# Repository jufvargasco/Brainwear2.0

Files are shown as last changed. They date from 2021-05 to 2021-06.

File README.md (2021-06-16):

# Brainwear board

The Brainwear board is an open-source EEG sensing driver module is designed with the state-of-the-art analog front-end that is pin-compatible with the popular Feather ecosystem in the wearable and DIY community.

## Hardware description

The Brainwear board was made using the Texas Instruments Analog Front-End ADS1299. This SOC incorporates low-power technology and integrates instrumentation amplifiers, operational amplifiers, and analog to digital converters into a single IC. Hence, it is ideal for biopotential measurements such as EEG, ECG, and EOG as it provides eight different channels with a 24-bit resolution and a sampling rate of 250 Hz. Additionally, it includes attractive characteristics such as test signals for impedance measurement and SPI compatible interface.

The Brainwear board is a mixed-signal system that combines both analog and digital components. Since both components are present in a single circuit, the analog circuit is susceptible to crosstalk noise generated by the digital circuit via stray capacitances. As a result, the small EEG signals acquired by the AFE can easily be distorted and provide erroneous measurements. The crosstalk noise was avoided by using a fully isolated circuit design technique. That is, separated ground planes for digital and analog signals and isolated analog and digital interfaces at each side of the board. Moreover, we used Low-Dropout linear regulators (MCP1754T-3302, TPS72325, TLV70025) and a voltage inverter (TCM828) to provide the analog bipolar supply of +- 2.5V and the digital supply of + 3.3V. The control signals of these devices were also isolated from the ground planes to avoid the switching noise generated by the voltage inverter.  

The feather board powers the Brainwear board. Then, a voltage detection IC (BD5330G) is used to disconnect the circuit once the supply voltage is lower than 3V to protect the battery. The ADS1299 is connected in a referential montage. Thus, eight different channels can be measured in reference to the input SRB1. The AFE also offers the possibility of measuring the bias in the signals using the Bias input included in the PCB. Electrostatic discharge chips were included to protect the channels of the board as well as the main analog and digital signals in the circuit.
Additionally, an LED (GPIO4) was added to provide an easy way to test the SPI communication between the main board and the Brainwear module. Hardware filters were included following the references provided by Texas Instruments and OpenBCI. Finally, an SD module was integrated into the board in order to record EEG data when required. It is essential to mention that the ADS1299 and the SD card do not share the same SPI bus. Hence, the ADS1299 is connected to the predetermined SPI pins of the feather board, while the SD card requires configuring the board's upper pins to act as an SPI bus.

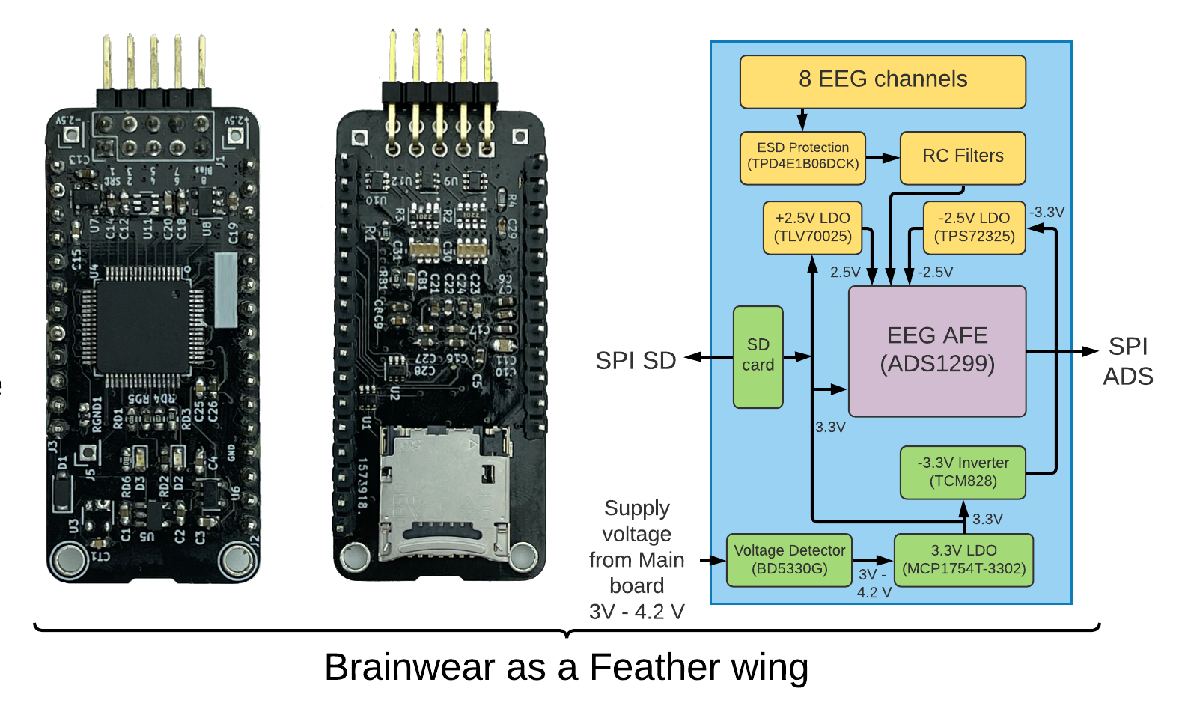
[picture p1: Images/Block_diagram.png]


The KiCAD files with the PCB of the Brainwear board are in the folder Design Files

## Firmware description
The firmware shows an application example in the file Brainwear_test.ino. The program contains two different types of classes: the first one is used for instantiating the Brainwear board while the second allows to add the Mechanomyography sensors whose signals are acquired with the TI-ADS1015. The first class packages all the functionalities available in the Brainwear hardware, i.e. testing signals, register, channel, and sample rate configuration, among others. This code is based on the OpenBCI firmware for the Cyton board. On the other hand, the second class allows to instantiate one board of the ADS1015 according to the required sample rate and gain. It also includes functionalities to send data to the main board according to the type of transmissions.

The system receives commands via the serial port that allow to configure the way the board behaves. A description of the commands is given below. Further information about the commands can be found in the file Brainwear_definitions.h

### Commands
#### Multichar commands
1. Channel settings

This command requires multiple characters to be recognized. It consists of seven different settings group together corresponding to the channel to modify, power-down, gain, type of input, bias generation, connection to SRB2, connection to SRB1, respectively. The code starts with lower x and end with capital X.

Example:
<p align="center">
    x1060001X
</p>

This code sets the channel (1) to power-down on (0), gain of 24 (6), normal input (0), remove bias (0), disconnected of SRB2 (0) and connected to SRB1 (1)

2. Leadoff settings

This command requires multiple characters to be recognized. It consists of 3 different settings group together corresponding to the channel to modify and the activation of the Lead off for the channel P and the channel N of the specified channel, respectively. The code starts with lower z and end with capital Z.

Example:
<p align="center">
    z111Z
</p>

This code sets the Leadoff detection for the channel (1) to (1 / activated) for the P channel and to (1 / activated) for the N channel.

3. Sample rate settings
 
This command requires multiple characters to be recognized. It consists of the character ~ followed by the desired sample rate for the board. The options are shown below.

| Command | Sample Rate |
|---------|-------------|
| 0       | 16 KHz      |
| 1       | 8 KHz       |
| 2       | 4 KHz       |
| 3       | 2 KHz       |
| 4       | 1 KHz       |
| 5       | 500 Hz      |
| 6       | 250 Hz      |

Example:
<p align="center">
    ~6
</p>

This code sets the sample rate of the board to 250 Hz.

#### Single commands

The single commands to manipulate the Brainwear board as described in the following table.

| Command | Description |
|---------|-------------|
| 1       | Deactivate channel 1      |
| 2       | Deactivate channel 2      |
| 3       | Deactivate channel 3      |
| 4       | Deactivate channel 4      |
| 5       | Deactivate channel 5      |
| 6       | Deactivate channel 6      |
| 7       | Deactivate channel 7      |
| 8       | Deactivate channel 8      |
| Q       | Activate channel 1        |
| W       | Activate channel 2        |
| E       | Activate channel 3        |
| R       | Activate channel 4        |
| T       | Activate channel 5        |
| Y       | Activate channel 6        |
| U       | Activate channel 7        |
| I       | Activate channel 8        |
| p       | Connect channels to DC Test signal      | 
| 0       | Connect channels to GND Test signal     | 
| =       | Connect channels to fast 1X Test signal | 
| -       | Connect channels to slow 1X signal      | 
| ]       | Connect channels to fast 2X Test signal | 
| \[      | Connect channels to slow 2X Test signal | 
| n       | Connect channels to normal input        | 
| d       | Set all channels to default settings      |
| D       | Report the default settings        |
| C       | Report number of channels in board      |
| t       | Activate serial stream of data       |
| y       | Deactivate serial stream of data       |
| b       | Start streaming data       |
| s       | Stop streaming data         |
| ?       | Show the register settings of the ADS1299 board       |
| v       | Soft reset of the board        |
| V       | Get firmware version        |
| l       | Turn on LED on the Brainwear board      |
| k       | Turn off LED on the Brainwear board      |
| a       | Activate recording with the SD card      |
| r       | Reset file counter for the SD files      |
| j       | Close SD file      |
| A       | Record 1 minute of activity in the SD      |
| S       | Record 5 minutes of activity in the SD       |
| F       | Record 15 minutes of activity in the SD      |
| G       | Record 30 minutes of activity in the SD         |
| H       | Record 1 hour of activity in the SD        |
| J       | Record 2 hours of activity in the SD        |
| K       | Record 4 hours of activity in the SD         |
| <       | Set transmission to RAW mode (compatible with OpenBCI)        |
| >       | Set transmission to ASCII mode (compatible with Arduino plotter)        |
| M       | Activate multimode (EEG + MMG)       |
| N       | Deactivate multimode  (Only EEG is active)       |

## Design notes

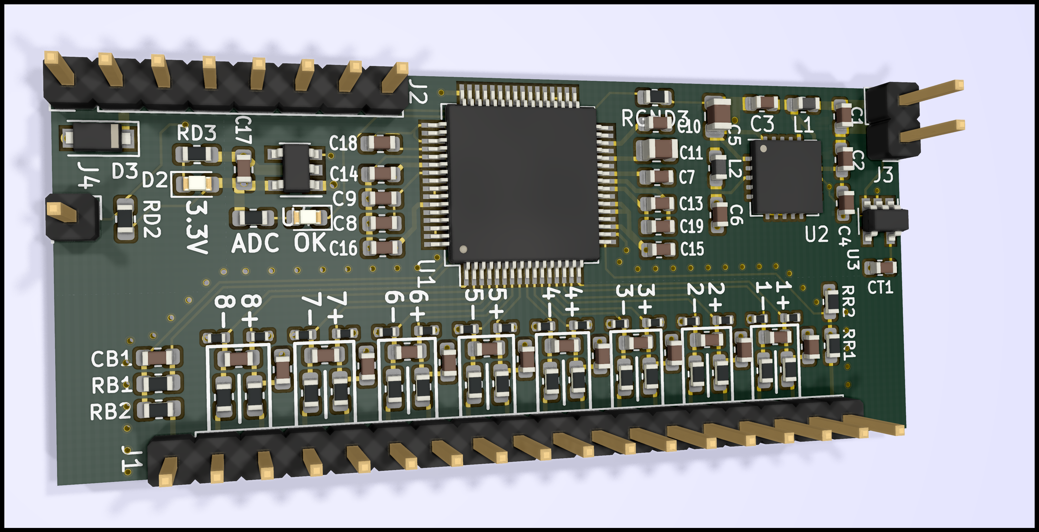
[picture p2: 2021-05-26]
Design files/front ray tracing.png

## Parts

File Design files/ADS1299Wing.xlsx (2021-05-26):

Id | Designator | Package | Quantity | Designation | Voltage | Supplier and ref
1 | -2.5V|+2.5V|J5 | PinHeader_1x01_P2.54mm_Vertical | 3 | Conn_01x01
2 | C1 | C_0603_1608Metric | 1 | 2.2uF | 16
3 | C2|C13|C14|C19|C20 | C_0603_1608Metric | 5 | 2.2uF | 6.3
4 | C10 | C_0805_2012Metric | 1 | 100uF | 6.3
5 | C15 | C_0603_1608Metric | 1 | 0.01uF | 16
6 | C18|C6|C3|C4|C12 | C_0603_1608Metric | 5 | 10uF | 4
7 | C29|CB1|CT1 | C_0603_1608Metric | 3 | 1nF | 16
8 | C31|C30 | CA064C102K5RACTU | 2 | CA064C102K5RACTU
9 | C5|C27|C9|C11|C16|C21|C23|C25 | C_0603_1608Metric | 8 | 1uF | 6.3
10 | C7|C17|C22|C24|C26|C28 | C_0603_1608Metric | 6 | 0.1uF | 16
11 | C8 | C_0603_1608Metric | 1 | 100nF | 16
12 | D1 | D_SOD-123F | 1 | MBR120
13 | D2|D3 | LED_0603_1608Metric | 2 | LED_Small
14 | J1 | PinHeader_2x05_P2.54mm_Vertical | 1 | Conn_02x05_Top_Bottom
15 | J2 | 1X16_ROUND_MIN | 1 | Conn_01x16
16 | J3 | 1X12_ROUND_MIN | 1 | Conn_01x12
17 | R2|R3 | RESCAF80P320X160X60-8N | 2 | CAY16-2201F4LF
18 | R4|R1 | R_0603_1608Metric | 2 | 2.2K
19 | RB1 | R_0603_1608Metric | 1 | 1MOhm
20 | RD1 | R_0603_1608Metric | 1 | 1M
21 | RD2 | R_0603_1608Metric | 1 | 470
22 | RD3|RD4|RD5 | R_0603_1608Metric | 3 | 10K
23 | RD6 | R_0603_1608Metric | 1 | 1k
24 | RGND1 | R_0603_1608Metric | 1 | R_Small
25 | U12|U1|U2|U9|U10|U11 | SOT-363_SC-70-6 | 6 | TPD4E1B06DCK
26 | U3 | SOT-23-5 | 1 | BD5332G
27 | U4 | TQFP-64_10x10mm_P0.5mm | 1 | ADS1299
28 | U5 | SOT95P280X145-5N | 1 | MCP1754T-3302E_OT
29 | U6 | SOT-23-5 | 1 | TCM828
30 | U7 | SOT-23-5 | 1 | TPS72325
31 | U8 | SOT-23-5 | 1 | TLV70025

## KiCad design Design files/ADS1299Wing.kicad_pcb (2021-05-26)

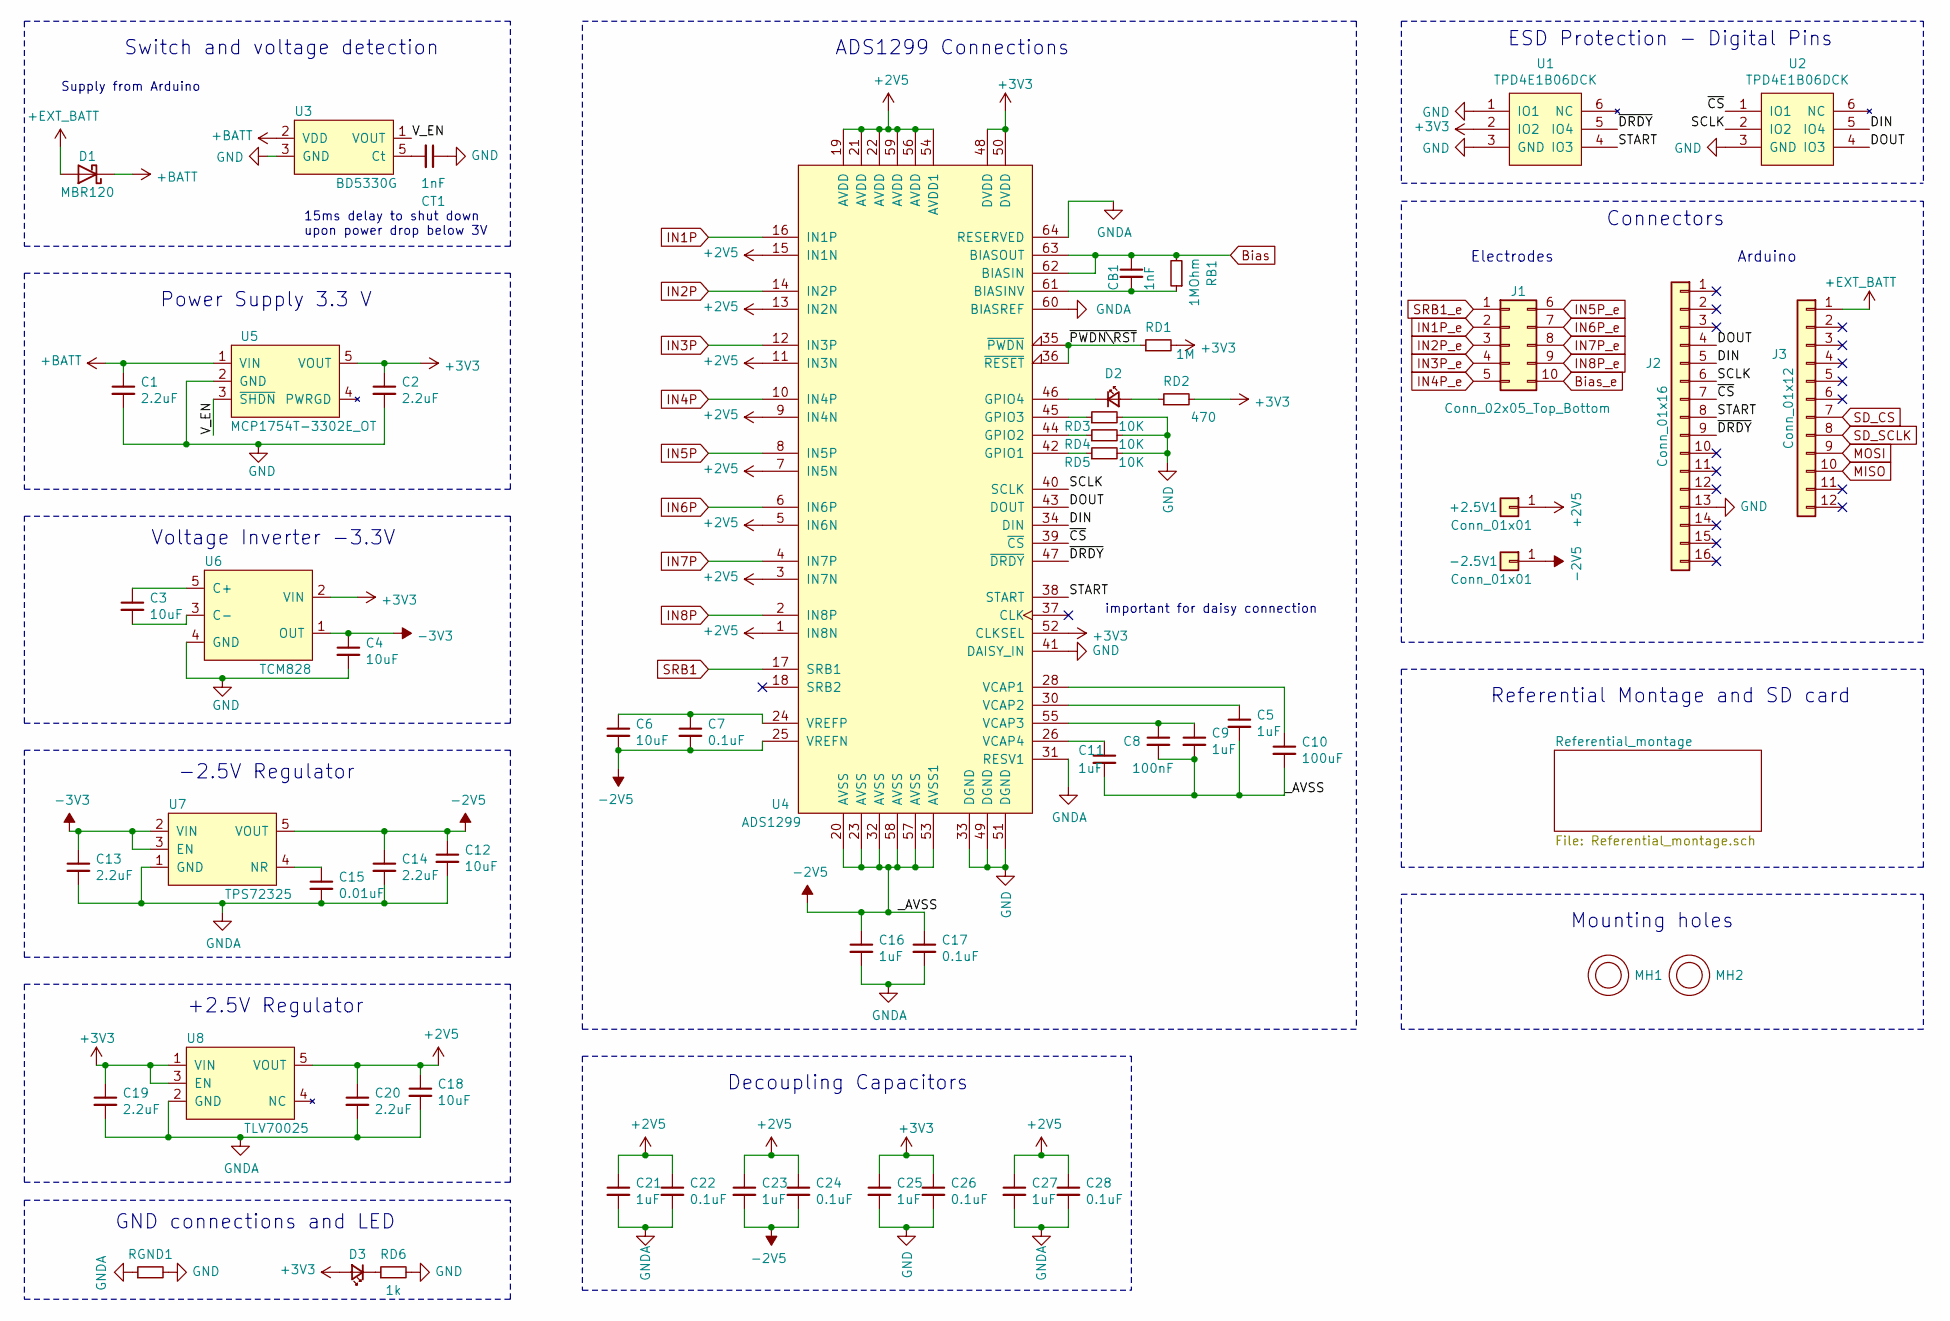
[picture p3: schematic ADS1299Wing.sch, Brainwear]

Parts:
+2.5V1: Conn_01x01; PinHeader_1x01_P2.54mm_Vertical
-2.5V1: Conn_01x01; PinHeader_1x01_P2.54mm_Vertical
C1, C2, C13, C14, C19, C20: 2.2uF; C_0603_1608Metric
C3, C4, C6, C12, C18: 10uF; C_0603_1608Metric
C5, C9, C11, C16, C21, C23, C25, C27: 1uF; C_0603_1608Metric
C7, C17, C22, C24, C26, C28: 0.1uF; C_0603_1608Metric
C8: 100nF; C_0603_1608Metric
C10: 100uF; C_0805_2012Metric
C15: 0.01uF; C_0603_1608Metric
CB1: 1nF; C_0603_1608Metric
CT1: 1nF; C_0603_1608Metric
D1: MBR120; D_SOD-123F
D2, D3: LED_Small; LED_0603_1608Metric
J1: Conn_02x05_Top_Bottom; PinHeader_2x05_P2.54mm_Vertical
J2: Conn_01x16; 1X16_ROUND_MIN
J3: Conn_01x12; 1X12_ROUND_MIN
MH1, MH2: M_HOLE2.5; MH2.5
RB1: 1MOhm; R_0603_1608Metric
RD1: 1M; R_0603_1608Metric
RD2: 470; R_0603_1608Metric
RD3, RD4, RD5: 10K; R_0603_1608Metric
RD6: 1k; R_0603_1608Metric
RGND1: R_Small; R_0603_1608Metric
U1, U2: TPD4E1B06DCK; SOT-363_SC-70-6
U3: BD5330G; SOT-23-5
U4: ADS1299; TQFP-64_10x10mm_P0.5mm
U5: MCP1754T-3302E_OT; SOT95P280X145-5N
U6: TCM828; SOT-23-5
U7: TPS72325; SOT-23-5
U8: TLV70025; SOT-23-5

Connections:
+2V5: +2.5V1.1, C18.1, C20.1, C21.1, C22.1, C23.1, C24.1, C27.1, C28.1, U4.1 (IN8N), U4.3 (IN7N), U4.5 (IN6N), U4.7 (IN5N), U4.9 (IN4N), U4.11 (IN3N), U4.13 (IN2N), U4.15 (IN1N), U4.19 (AVDD), U4.21 (AVDD), U4.22 (AVDD), U4.54 (AVDD1), U4.56 (AVDD), U4.59 (AVDD), U8.5 (VOUT); also elsewhere on the board
+3V3: C2.1, C19.1, C25.1, C26.1, D3.2 (A), RD1.2, RD2.2, U1.2 (IO2), U4.48 (DVDD), U4.50 (DVDD), U4.52 (CLKSEL), U5.5 (VOUT), U6.2 (VIN), U8.1 (VIN), U8.3 (EN); also elsewhere on the board
+BATT: C1.1, D1.1 (K), U3.2 (VDD), U5.1 (VIN)
+EXT_BATT: D1.2 (A), J3.1
-2V5: -2.5V1.1, C5.2, C6.2, C7.2, C8.2, C9.2, C10.2, C11.2, C12.1, C14.1, C16.1, C17.1, C23.2, C24.2, U4.20 (AVSS), U4.23 (AVSS), U4.25 (VREFN), U4.32 (AVSS), U4.53 (AVSS1), U4.57 (AVSS), U4.58 (AVSS), U7.5 (VOUT); also elsewhere on the board
-3V3: C4.1, C13.1, U6.1 (OUT), U7.2 (VIN), U7.3 (EN)
/DIN: J2.5, U2.5 (IO4), U4.34 (DIN)
/DOUT: J2.4, U2.4 (IO3), U4.43 (DOUT)
/SCLK: J2.6, U2.2 (IO2), U4.40 (SCLK)
/START: J2.8, U1.4 (IO3), U4.38 (START)
/V_EN: U3.1 (VOUT), U5.3 (~SHDN)
/~CS: J2.7, U2.1 (IO1), U4.39 (~CS)
/~DRDY: J2.9, U1.5 (IO4), U4.47 (~DRDY)
/~PWDN\RST: RD1.1, U4.35 (~PWDN), U4.36 (~RESET)
Bias: CB1.1, RB1.2, U4.62 (BIASIN), U4.63 (BIASOUT); also elsewhere on the board
Bias_e: J1.10; also elsewhere on the board
GND: C1.2, C2.2, C4.2, C25.2, C26.2, CT1.1, J2.13, RD3.2, RD4.2, RD5.2, RD6.2, RGND1.2, U1.1 (IO1), U1.3 (GND), U2.3 (GND), U3.3 (GND), U4.33 (DGND), U4.41 (DAISY_IN), U4.49 (DGND), U4.51 (DGND), U5.2 (GND), U6.4 (GND); also elsewhere on the board
GNDA: C12.2, C13.2, C14.2, C15.2, C16.2, C17.2, C18.2, C19.2, C20.2, C21.2, C22.2, C27.2, C28.2, RGND1.1, U4.31 (RESV1), U4.60 (BIASREF), U4.64 (RESERVED), U7.1 (GND), U8.2 (GND); also elsewhere on the board
IN1P: U4.16 (IN1P); also elsewhere on the board
IN1P_e: J1.2; also elsewhere on the board
IN2P: U4.14 (IN2P); also elsewhere on the board
IN2P_e: J1.3; also elsewhere on the board
IN3P: U4.12 (IN3P); also elsewhere on the board
IN3P_e: J1.4; also elsewhere on the board
IN4P: U4.10 (IN4P); also elsewhere on the board
IN4P_e: J1.5; also elsewhere on the board
IN5P: U4.8 (IN5P); also elsewhere on the board
IN5P_e: J1.6; also elsewhere on the board
IN6P: U4.6 (IN6P); also elsewhere on the board
IN6P_e: J1.7; also elsewhere on the board
IN7P: U4.4 (IN7P); also elsewhere on the board
IN7P_e: J1.8; also elsewhere on the board
IN8P: U4.2 (IN8P); also elsewhere on the board
IN8P_e: J1.9; also elsewhere on the board
MISO: J3.10; also elsewhere on the board
MOSI: J3.9; also elsewhere on the board
unnamed: C3.1, U6.5 (C+)
unnamed: C3.2, U6.3 (C-)
unnamed: C5.1, U4.30 (VCAP2)
unnamed: C6.1, C7.1, U4.24 (VREFP)
unnamed: C8.1, C9.1, U4.55 (VCAP3)
unnamed: C10.1, U4.28 (VCAP1)
unnamed: C11.1, U4.26 (VCAP4)
unnamed: C15.1, U7.4 (NR)
unnamed: CB1.2, RB1.1, U4.61 (BIASINV)
unnamed: CT1.2, U3.5 (Ct)
unnamed: D2.1 (K), U4.46 (GPIO4)
unnamed: D2.2 (A), RD2.1
unnamed: D3.1 (K), RD6.1
unnamed: RD3.1, U4.45 (GPIO3)
unnamed: RD4.1, U4.44 (GPIO2)
unnamed: RD5.1, U4.42 (GPIO1)
SD_CS: J3.7; also elsewhere on the board
SD_SCLK: J3.8; also elsewhere on the board
SRB1: U4.17 (SRB1); also elsewhere on the board
SRB1_e: J1.1; also elsewhere on the board

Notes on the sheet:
15ms delay to shut down upon power drop below 3V
Power Supply 3.3 V
Switch and voltage detection
Voltage Inverter -3.3V
-2.5V Regulator
+2.5V Regulator
ADS1299 Connections
ESD Protection - Digital Pins
GND connections and LED
Connectors
Electrodes
Arduino
important for daisy connection
Supply from Arduino
Referential Montage and SD card
Decoupling Capacitors
Mounting holes

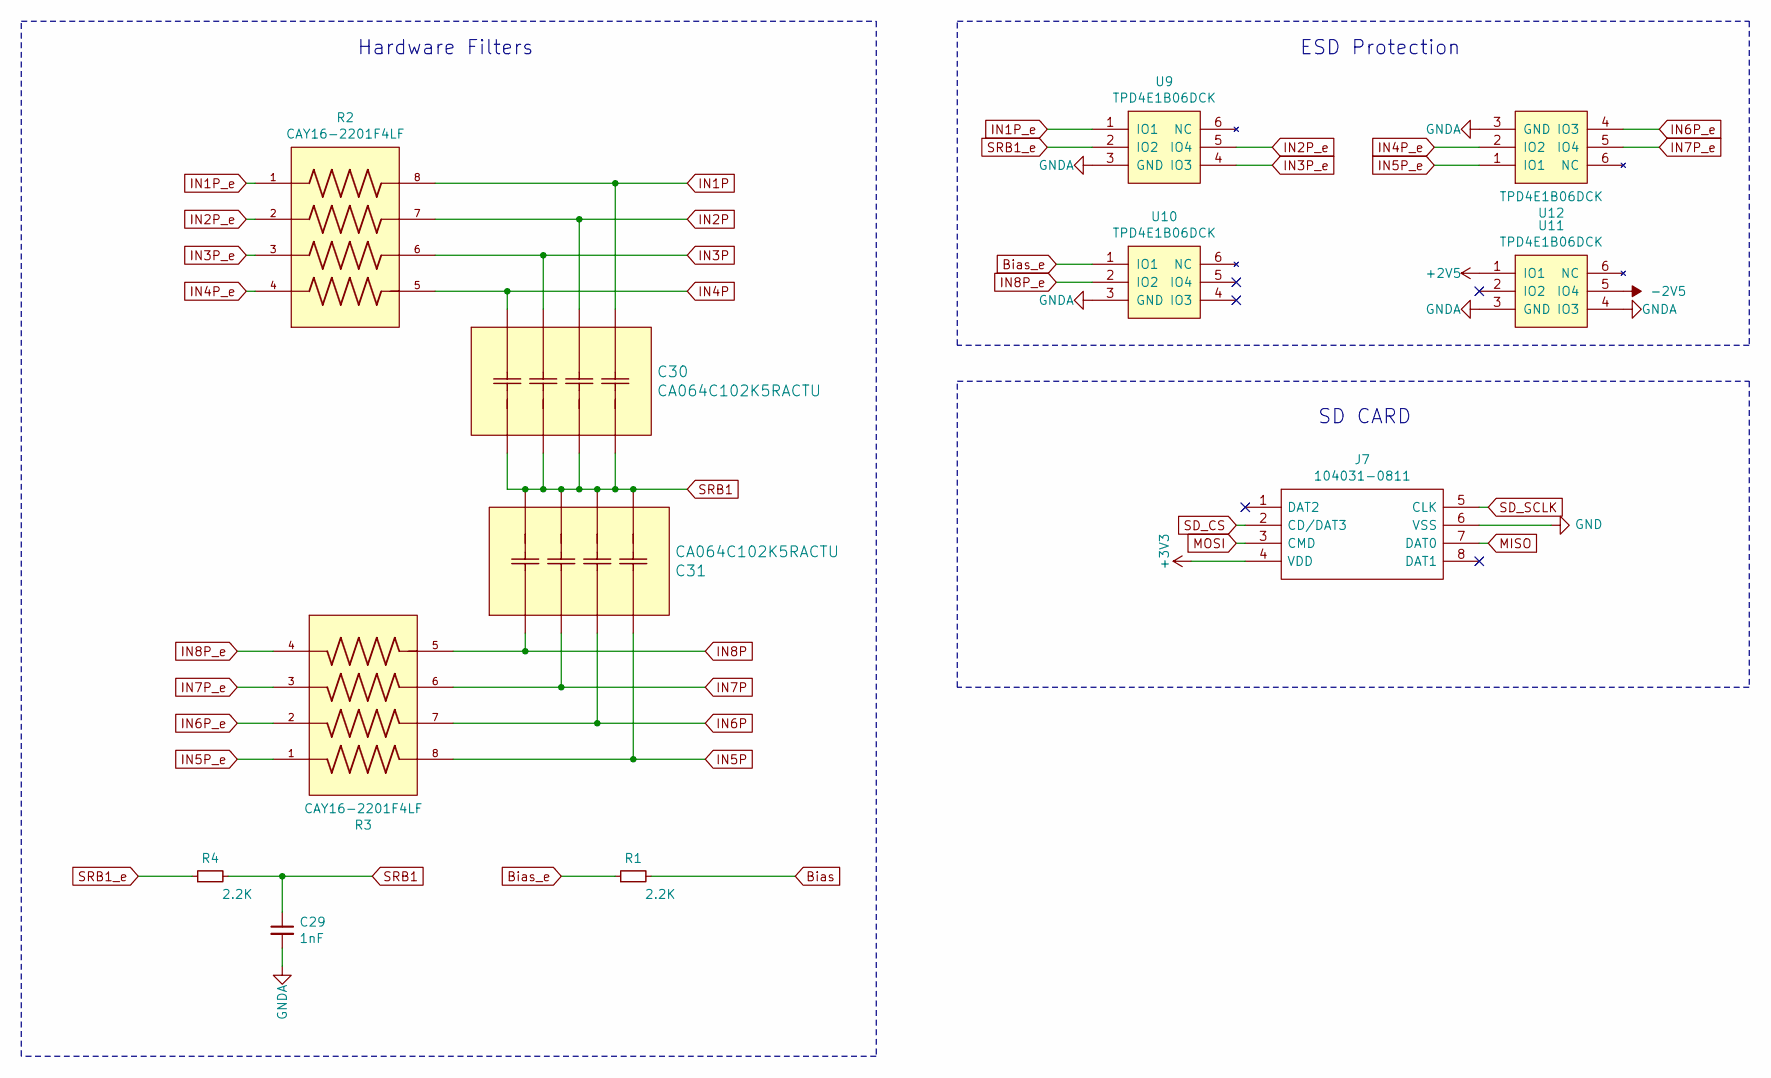
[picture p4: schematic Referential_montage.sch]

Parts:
C29: 1nF; C_0603_1608Metric
C30, C31: CA064C102K5RACTU
J7: 104031-0811; 1040310811; Mouser Part Number 538-104031-0811
R1, R4: 2.2K; R_0603_1608Metric
R2, R3: CAY16-2201F4LF; RESCAF80P320X160X60-8N
U9, U10, U11, U12: TPD4E1B06DCK; SOT-363_SC-70-6

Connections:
+2V5: U11.1 (IO1); also elsewhere on the board
+3V3: J7.4 (VDD); also elsewhere on the board
-2V5: U11.5 (IO4); also elsewhere on the board
Bias: R1.2; also elsewhere on the board
Bias_e: R1.1, U10.1 (IO1); also elsewhere on the board
GND: J7.6 (VSS); also elsewhere on the board
GNDA: C29.2, U9.3 (GND), U10.3 (GND), U11.3 (GND), U11.4 (IO3), U12.3 (GND); also elsewhere on the board
IN1P: C30.1, R2.8; also elsewhere on the board
IN1P_e: R2.1, U9.1 (IO1); also elsewhere on the board
IN2P: C30.2, R2.7; also elsewhere on the board
IN2P_e: R2.2, U9.5 (IO4); also elsewhere on the board
IN3P: C30.3, R2.6; also elsewhere on the board
IN3P_e: R2.3, U9.4 (IO3); also elsewhere on the board
IN4P: C30.4, R2.5; also elsewhere on the board
IN4P_e: R2.4, U12.2 (IO2); also elsewhere on the board
IN5P: C31.1, R3.8; also elsewhere on the board
IN5P_e: R3.1, U12.1 (IO1); also elsewhere on the board
IN6P: C31.2, R3.7; also elsewhere on the board
IN6P_e: R3.2, U12.4 (IO3); also elsewhere on the board
IN7P: C31.3, R3.6; also elsewhere on the board
IN7P_e: R3.3, U12.5 (IO4); also elsewhere on the board
IN8P: C31.4, R3.5; also elsewhere on the board
IN8P_e: R3.4, U10.2 (IO2); also elsewhere on the board
MISO: J7.7 (DAT0); also elsewhere on the board
MOSI: J7.3 (CMD); also elsewhere on the board
SD_CS: J7.2 (CD/DAT3); also elsewhere on the board
SD_SCLK: J7.5 (CLK); also elsewhere on the board
SRB1: C29.1, C30.5, C30.6, C30.7, C30.8, C31.5, C31.6, C31.7, C31.8, R4.2; also elsewhere on the board
SRB1_e: R4.1, U9.2 (IO2); also elsewhere on the board

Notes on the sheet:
Hardware Filters
ESD Protection
SD CARD

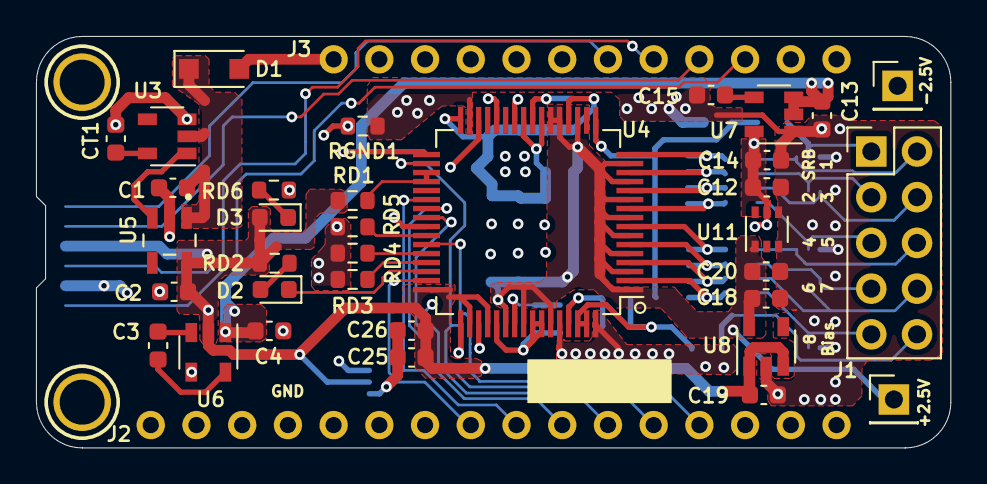
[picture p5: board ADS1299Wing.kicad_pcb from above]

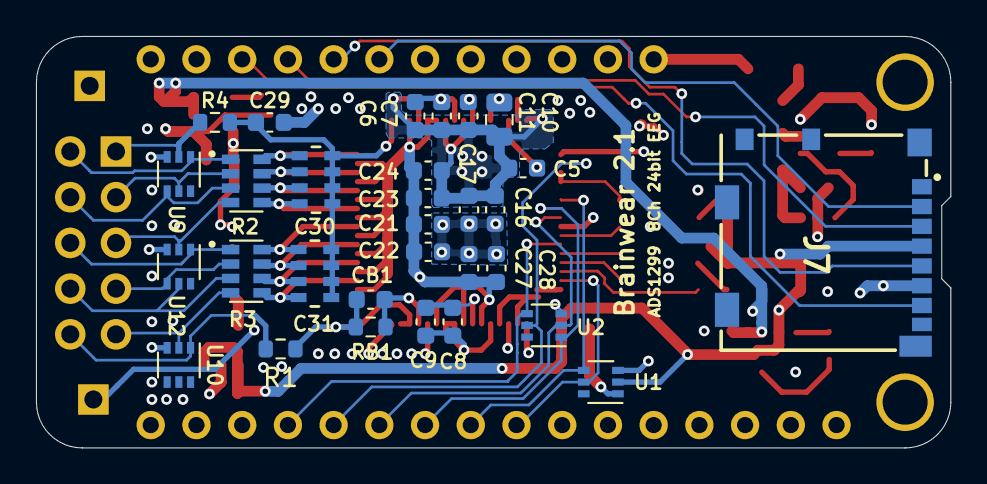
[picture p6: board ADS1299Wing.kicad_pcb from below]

Board: 4 copper layers, 50.8 x 22.9 mm, 68 parts (30 on the bottom side), 56 nets.

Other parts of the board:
+2.5V: Conn_01x01; PinHeader_1x01_P2.54mm_Vertical
-2.5V: Conn_01x01; PinHeader_1x01_P2.54mm_Vertical

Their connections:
+2V5: +2.5V.1; also elsewhere on the board
-2V5: -2.5V.1; also elsewhere on the board

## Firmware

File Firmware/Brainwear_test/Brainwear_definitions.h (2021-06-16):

//
// Created by jpipe on 2/26/2021.
//

#ifndef SOFTWARE_BRAINWEAR_DEFINITIONS_H
#define SOFTWARE_BRAINWEAR_DEFINITIONS_H

// Pin connections Huzzah 32 feather
#define CS        4
#define DRDY      39
#define START_PIN 36

#define SD_SCL     15
#define SD_MISO    14
#define SD_MOSI    32
#define SD_SS      33

// Baud rates
#define BAUD_RATE 115200

// File transmissions
#define ADS_BOP 0xA0 // Beginning of stream packet
#define ADS_EOP 0xC0 // Beginning of stream packet

//Address od ADS1X15
#define ADS1x15_1  0x49  // Used for FSR
#define ADS1x15_2  0x4A  // Used for piezos

//SPI Command Definitions (pg. 35)
#define _WAKEUP   0b00000010     // Wake-up from standby mode
#define _STANDBY  0b00000100   // Enter Standby mode
#define _RESET    0b00000110   // Reset the device
#define _START    0b00001000   // Start and restart (synchronize) conversions
#define _STOP     0b00001010   // Stop conversion
#define _RDATAC   0b00010000   // Enable Read Data Continuous mode (default mode at power-up)
#define _SDATAC   0b00010001   // Stop Read Data Continuous mode
#define _RDATA    0b00010010   // Read data by command; supports multiple read back

#define _RREG 0x20 // (also = 00100000) is the first opcode that the address must be added to for RREG communication
#define _WREG 0x40 // 01000000 in binary (Datasheet, pg. 35)

//ADS1299 Register Addressess
#define ID_REG      0x00  // this register contains ADS_ID
#define CONFIG1     0x01
#define CONFIG2     0x02
#define CONFIG3     0x03
#define LOFF        0x04
#define CH1SET      0x05
#define CH2SET      0x06
#define CH3SET      0x07
#define CH4SET      0x08
#define CH5SET      0x09
#define CH6SET      0x0A
#define CH7SET      0x0B
#define CH8SET      0x0C
#define BIAS_SENSP  0x0D
#define BIAS_SENSN  0x0E
#define LOFF_SENSP  0x0F
#define LOFF_SENSN  0x10
#define LOFF_FLIP   0x11
#define LOFF_STATP  0x12
#define LOFF_STATN  0x13
#define GPIO        0x14
#define MISC1       0x15
#define MISC2       0x16
#define CONFIG4     0x17

//Channel Settings
#define POWER_DOWN      (0)
#define GAIN_SET        (1)
#define INPUT_TYPE_SET  (2)
#define BIAS_SET        (3)
#define SRB2_SET        (4)
#define SRB1_SET        (5)
#define YES      	    (0x01)
#define NO      	    (0x00)

//gainCode choices
#define ADS_GAIN01 (0b00000000)	// 0x00
#define ADS_GAIN02 (0b00010000)	// 0x10
#define ADS_GAIN04 (0b00100000)	// 0x20
#define ADS_GAIN06 (0b00110000)	// 0x30
#define ADS_GAIN08 (0b01000000)	// 0x40
#define ADS_GAIN12 (0b01010000)	// 0x50
#define ADS_GAIN24 (0b01100000)	// 0x60
#define ADS_NOGAIN (0b01110000) // 0x70

//inputType choices
#define ADSINPUT_NORMAL     (0b00000000)
#define ADSINPUT_SHORTED    (0b00000001)
#define ADSINPUT_BIAS_MEAS  (0b00000010)
#define ADSINPUT_MVDD       (0b00000011)
#define ADSINPUT_TEMP       (0b00000100)
#define ADSINPUT_TESTSIG    (0b00000101)
#define ADSINPUT_BIAS_DRP   (0b00000110)
#define ADSINPUT_BIAL_DRN   (0b00000111)

//Number of channels
#define ADS_NUM_CHANNELS         8
#define ADS_CHANNELS_BOARD       4
#define ADS_BYTES_PER_CHAN       3
#define ADS_BYTES_PER_ADS_SAMPLE 24

//Number of additional channels for ADC Data (ADS1115)
#define MMG_CHANNELS     4
#define MMG_BOARDS       2

//Useful numbers
#define NUMBER_OF_BOARD_SETTINGS     1
#define NUMBER_OF_CHANNEL_SETTINGS   6
#define NUMBER_OF_LEAD_OFF_SETTINGS  2

//Lead-off signal choices
#define LOFF_MAG_6NA        (0b00000000)
#define LOFF_MAG_24NA       (0b00000100)
#define LOFF_MAG_6UA        (0b00001000)
#define LOFF_MAG_24UA       (0b00001100)
#define LOFF_FREQ_DC        (0b00000000)
#define LOFF_FREQ_7p8HZ     (0b00000001)
#define LOFF_FREQ_31p2HZ    (0b00000010)
#define LOFF_FREQ_FS_4      (0b00000011)
#define PCHAN (0)
#define NCHAN (1)
#define OFF (0)
#define ON (1)

//Settings
#define DEFAULT_CONFIG1     (0b10010000)

//test signal choices CONFIG2...ADS1299 datasheet page 47
#define ADSTESTSIG_AMP_1X       (0b00000000)
#define ADSTESTSIG_AMP_2X       (0b00000100)
#define ADSTESTSIG_PULSE_SLOW   (0b00000000)
#define ADSTESTSIG_PULSE_FAST   (0b00000001)
#define ADSTESTSIG_DCSIG        (0b00000011)
#define ADSTESTSIG_NOCHANGE     (0b11111111)

//COMMANDS TO CONTROL BOARD
/** Time out for multi char commands **/
#define MULTI_CHAR_COMMAND_TIMEOUT_MS 1000

/** Channel Setting Commands */
#define ADS_NUMBER_OF_BYTES_SETTINGS_CHANNEL 9
#define ADS_CHANNEL_CMD_SET             'x'
#define ADS_CHANNEL_CMD_LATCH           'X'
//Choose channel
#define ADS_CHANNEL_CMD_CHANNEL_1       '1'
#define ADS_CHANNEL_CMD_CHANNEL_2       '2'
#define ADS_CHANNEL_CMD_CHANNEL_3       '3'
#define ADS_CHANNEL_CMD_CHANNEL_4       '4'
#define ADS_CHANNEL_CMD_CHANNEL_5       '5'
#define ADS_CHANNEL_CMD_CHANNEL_6       '6'
#define ADS_CHANNEL_CMD_CHANNEL_7       '7'
#define ADS_CHANNEL_CMD_CHANNEL_8       '8'
//Power-down
#define ADS_CHANNEL_CMD_POWER_ON        '0'
#define ADS_CHANNEL_CMD_POWER_OFF       '1'
// PGA gain
#define ADS_CHANNEL_CMD_GAIN_1          '0'
#define ADS_CHANNEL_CMD_GAIN_2          '1'
#define ADS_CHANNEL_CMD_GAIN_4          '2'
#define ADS_CHANNEL_CMD_GAIN_6          '3'
#define ADS_CHANNEL_CMD_GAIN_8          '4'
#define ADS_CHANNEL_CMD_GAIN_12         '5'
#define ADS_CHANNEL_CMD_GAIN_24         '6'
//Channel input
#define ADS_CHANNEL_CMD_ADC_Normal      '0'
#define ADS_CHANNEL_CMD_ADC_Shorted     '1'
#define ADS_CHANNEL_CMD_ADC_BiasMethod  '2'
#define ADS_CHANNEL_CMD_ADC_MVDD        '3'
#define ADS_CHANNEL_CMD_ADC_Temp        '4'
#define ADS_CHANNEL_CMD_ADC_TestSig     '5'
#define ADS_CHANNEL_CMD_ADC_BiasDRP     '6'
#define ADS_CHANNEL_CMD_ADC_BiasDRN     '7'
//Bias generation
#define ADS_CHANNEL_CMD_BIAS_REMOVE     '0'
#define ADS_CHANNEL_CMD_BIAS_INCLUDE    '1'
// SRB2 connection
#define ADS_CHANNEL_CMD_SRB2_DISCONNECT '0'
#define ADS_CHANNEL_CMD_SRB2_CONNECT    '1'
//SRB1 connection
#define ADS_CHANNEL_CMD_SRB1_DISCONNECT '0'
#define ADS_CHANNEL_CMD_SRB1_CONNECT    '1'

/** LeadOff Impedance Commands */
#define ADS_NUMBER_OF_BYTES_SETTINGS_LEAD_OFF 5
#define ADS_CHANNEL_IMPEDANCE_SET                     'z'
#define ADS_CHANNEL_IMPEDANCE_LATCH                   'Z'

#define ADS_CHANNEL_IMPEDANCE_TEST_SIGNAL_APPLIED     '1'
#define ADS_CHANNEL_IMPEDANCE_TEST_SIGNAL_APPLIED_NOT '0'

/** Set sample rate */
#define ADS_SAMPLE_RATE_SET '~'

/** Turning channels off */
#define ADS_CHANNEL_OFF_1 '1'
#define ADS_CHANNEL_OFF_2 '2'
#define ADS_CHANNEL_OFF_3 '3'
#define ADS_CHANNEL_OFF_4 '4'
#define ADS_CHANNEL_OFF_5 '5'
#define ADS_CHANNEL_OFF_6 '6'
#define ADS_CHANNEL_OFF_7 '7'
#define ADS_CHANNEL_OFF_8 '8'

/** Turn channels on */
#define ADS_CHANNEL_ON_1 'Q'
#define ADS_CHANNEL_ON_2 'W'
#define ADS_CHANNEL_ON_3 'E'
#define ADS_CHANNEL_ON_4 'R'
#define ADS_CHANNEL_ON_5 'T'
#define ADS_CHANNEL_ON_6 'Y'
#define ADS_CHANNEL_ON_7 'U'
#define ADS_CHANNEL_ON_8 'I'

/** Test Signal Control Commands
 * 1x - Voltage will be 1 * (VREFP - VREFN) / 2.4 mV
 * 2x - Voltage will be 2 * (VREFP - VREFN) / 2.4 mV
 */
#define ADS_TEST_SIGNAL_CONNECT_TO_DC            'p'
#define ADS_TEST_SIGNAL_CONNECT_TO_GROUND        '0'
#define ADS_TEST_SIGNAL_CONNECT_TO_PULSE_1X_FAST '='
#define ADS_TEST_SIGNAL_CONNECT_TO_PULSE_1X_SLOW '-'
#define ADS_TEST_SIGNAL_CONNECT_TO_PULSE_2X_FAST ']'
#define ADS_TEST_SIGNAL_CONNECT_TO_PULSE_2X_SLOW '['
#define ADS_NORMAL_INPUT                         'n'

/** Default Channel Settings */
#define ADS_CHANNEL_DEFAULT_ALL_SET 'd'
#define ADS_CHANNEL_DEFAULT_ALL_REPORT 'D'

/** Default Channel Settings */
#define ADS_NUMBER_CHANNELS    'C'

/** Stream Data Commands */
#define ADS_ACTIVATE_SERIAL_STREAM  't'
#define ADS_DEACTIVATE_SERIAL_STREAM  'y'
#define ADS_STREAM_START  'b'
#define ADS_STREAM_STOP   's'

/** Miscellaneous */
#define ADS_MISC_QUERY_REGISTER_SETTINGS '?'
#define ADS_MISC_SOFT_RESET              'v'
#define ADS_GET_VERSION                  'V'

/** Turn On/Off LED */
#define ADS_TURN_ON_LED  'l'
#define ADS_TURN_OFF_LED 'k'

/** SD Setting Commands */
#define ADS_INIT_SD         'a'
#define ADS_RST_SDCOUNT     'r'
#define ADS_CLOSE_SDFILE    'j'
#define ADS_SD_1MIN         'A'
#define ADS_SD_5MIN         'S'
#define ADS_SD_15MIN         'F'
#define ADS_SD_30MIN         'G'
#define ADS_SD_1HR         'H'
#define ADS_SD_2HR         'J'
#define ADS_SD_4HR         'K'

/** board Commands */
#define ADS_TX_RAW         '<'
#define ADS_TX_ASCII       '>'
#define ADS_MULTMODE_ON    'M'
#define ADS_MULTMODE_OFF   'N'


#endif //SOFTWARE_BRAINWEAR_DEFINITIONS_H

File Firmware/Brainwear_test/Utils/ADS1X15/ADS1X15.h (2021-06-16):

/**************************************************************************/
/*!
    @file     Adafruit_ADS1015.h
    @author   K. Townsend (Adafruit Industries)
    @license  BSD (see license.txt)

    This is a library for the Adafruit ADS1015 breakout board
    ----> https://www.adafruit.com/products/???

    Adafruit invests time and resources providing this open source code,
    please support Adafruit and open-source hardware by purchasing
    products from Adafruit!

    @section  HISTORY

    v1.0  - First release
    v1.1  - Added ADS1115 support - W. Earl
    v1.2  - Modified by Dennis Cabell.  See details in ccp file.
*/
/**************************************************************************/

#ifndef _ADS1X15_H
#define _ADS1X15_H

#if ARDUINO >= 100
 #include "Arduino.h"
#else
 #include "WProgram.h"
#endif

#include <Wire.h>

/*=========================================================================
    I2C ADDRESS/BITS
    -----------------------------------------------------------------------*/
    #define ADS1X15_ADDRESS                 (0x48)    // 1001 000 (ADDR = GND)
    #define HIGH_SPEED_MODE  (0x08)
/*=========================================================================*/

/*=========================================================================
    Default thresholds for comparator
    -----------------------------------------------------------------------*/
    #define ADS1X15_LOW_THRESHOLD_DEFAULT   (0x8000)
    #define ADS1X15_HIGH_THRESHOLD_DEFAULT  (0x7FFF)
/*=========================================================================*/

/*=========================================================================
    POINTER REGISTER
    -----------------------------------------------------------------------*/
    #define ADS1X15_REG_POINTER_MASK        (0x03)
    #define ADS1X15_REG_POINTER_CONVERT     (0x00)
    #define ADS1X15_REG_POINTER_CONFIG      (0x01)
    #define ADS1X15_REG_POINTER_LOWTHRESH   (0x02)
    #define ADS1X15_REG_POINTER_HITHRESH    (0x03)
/*=========================================================================*/

/*=========================================================================
    CONFIG REGISTER
    -----------------------------------------------------------------------*/
    #define ADS1X15_REG_CONFIG_OS_MASK      (0x8000)
    #define ADS1X15_REG_CONFIG_OS_SINGLE    (0x8000)  // Write: Set to start a single-conversion
    #define ADS1X15_REG_CONFIG_OS_BUSY      (0x0000)  // Read: Bit = 0 when conversion is in progress
    #define ADS1X15_REG_CONFIG_OS_NOTBUSY   (0x8000)  // Read: Bit = 1 when device is not performing a conversion

    #define ADS1X15_REG_CONFIG_MUX_MASK     (0x7000)
    #define ADS1X15_REG_CONFIG_MUX_DIFF_0_1 (0x0000)  // Differential P = AIN0, N = AIN1 (default)
    #define ADS1X15_REG_CONFIG_MUX_DIFF_0_3 (0x1000)  // Differential P = AIN0, N = AIN3
    #define ADS1X15_REG_CONFIG_MUX_DIFF_1_3 (0x2000)  // Differential P = AIN1, N = AIN3
    #define ADS1X15_REG_CONFIG_MUX_DIFF_2_3 (0x3000)  // Differential P = AIN2, N = AIN3
    #define ADS1X15_REG_CONFIG_MUX_SINGLE_0 (0x4000)  // Single-ended AIN0
    #define ADS1X15_REG_CONFIG_MUX_SINGLE_1 (0x5000)  // Single-ended AIN1
    #define ADS1X15_REG_CONFIG_MUX_SINGLE_2 (0x6000)  // Single-ended AIN2
    #define ADS1X15_REG_CONFIG_MUX_SINGLE_3 (0x7000)  // Single-ended AIN3

    #define ADS1X15_REG_CONFIG_PGA_MASK     (0x0E00)
    #define ADS1X15_REG_CONFIG_PGA_6_144V   (0x0000)  // +/-6.144V range = Gain 2/3
    #define ADS1X15_REG_CONFIG_PGA_4_096V   (0x0200)  // +/-4.096V range = Gain 1
    #define ADS1X15_REG_CONFIG_PGA_2_048V   (0x0400)  // +/-2.048V range = Gain 2 (default)
    #define ADS1X15_REG_CONFIG_PGA_1_024V   (0x0600)  // +/-1.024V range = Gain 4
    #define ADS1X15_REG_CONFIG_PGA_0_512V   (0x0800)  // +/-0.512V range = Gain 8
    #define ADS1X15_REG_CONFIG_PGA_0_256V   (0x0A00)  // +/-0.256V range = Gain 16

    #define ADS1X15_REG_CONFIG_MODE_MASK    (0x0100)
    #define ADS1X15_REG_CONFIG_MODE_CONTIN  (0x0000)  // Continuous conversion mode
    #define ADS1X15_REG_CONFIG_MODE_SINGLE  (0x0100)  // Power-down single-shot mode (default)

    #define ADS1015_REG_CONFIG_DR_MASK      (0x00E0)  
    #define ADS1015_REG_CONFIG_DR_128SPS    (0x0000)  // 128 samples per second
    #define ADS1015_REG_CONFIG_DR_250SPS    (0x0020)  // 250 samples per second
    #define ADS1015_REG_CONFIG_DR_490SPS    (0x0040)  // 490 samples per second
    #define ADS1015_REG_CONFIG_DR_920SPS    (0x0060)  // 920 samples per second
    #define ADS1015_REG_CONFIG_DR_1600SPS   (0x0080)  // 1600 samples per second (default)
    #define ADS1015_REG_CONFIG_DR_2400SPS   (0x00A0)  // 2400 samples per second
    #define ADS1015_REG_CONFIG_DR_3300SPS   (0x00C0)  // 3300 samples per second

    #define ADS1115_REG_CONFIG_DR_8SPS      (0x0000)  // 8 samples per second
    #define ADS1115_REG_CONFIG_DR_16SPS     (0x0020)  // 16 samples per second
    #define ADS1115_REG_CONFIG_DR_32SPS     (0x0040)  // 32 samples per second
    #define ADS1115_REG_CONFIG_DR_64SPS     (0x0060)  // 64 samples per second
    #define ADS1115_REG_CONFIG_DR_128SPS    (0x0080)  // 128 samples per second (default)
    #define ADS1115_REG_CONFIG_DR_250SPS    (0x00A0)  // 250 samples per second
    #define ADS1115_REG_CONFIG_DR_475SPS    (0x00C0)  // 475 samples per second
    #define ADS1115_REG_CONFIG_DR_860SPS    (0x00E0)  // 860 samples per second

    #define ADS1X15_REG_CONFIG_CMODE_MASK   (0x0010)
    #define ADS1X15_REG_CONFIG_CMODE_TRAD   (0x0000)  // Traditional comparator with hysteresis (default)
    #define ADS1X15_REG_CONFIG_CMODE_WINDOW (0x0010)  // Window comparator

    #define ADS1X15_REG_CONFIG_CPOL_MASK    (0x0008)
    #define ADS1X15_REG_CONFIG_CPOL_ACTVLOW (0x0000)  // ALERT/RDY pin is low when active (default)
    #define ADS1X15_REG_CONFIG_CPOL_ACTVHI  (0x0008)  // ALERT/RDY pin is high when active

    #define ADS1X15_REG_CONFIG_CLAT_MASK    (0x0004)  // Determines if ALERT/RDY pin latches once asserted
    #define ADS1X15_REG_CONFIG_CLAT_NONLAT  (0x0000)  // Non-latching comparator (default)
    #define ADS1X15_REG_CONFIG_CLAT_LATCH   (0x0004)  // Latching comparator
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

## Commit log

2021-05-26 Addition of Hardware files
    [ADS1299Wing-B_Cu.gbl, ADS1299Wing-B_Mask.gbs, ADS1299Wing-B_Paste.gbp, ADS1299Wing-B_SilkS.gbo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]
2021-06-16 Modification of Gerber files
    [ADS1299Wing-B_Cu.gbl, ADS1299Wing-B_Mask.gbs, ADS1299Wing-B_Paste.gbp, ADS1299Wing-B_SilkS.gbo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]

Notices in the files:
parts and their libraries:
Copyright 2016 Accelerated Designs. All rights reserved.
